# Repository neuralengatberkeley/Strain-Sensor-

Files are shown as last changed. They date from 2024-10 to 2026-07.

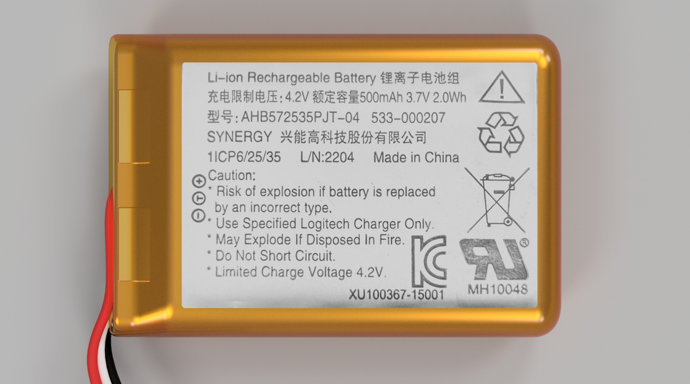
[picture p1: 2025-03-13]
CAD Files/tom sensor assembly/Renders/Battery 3.png

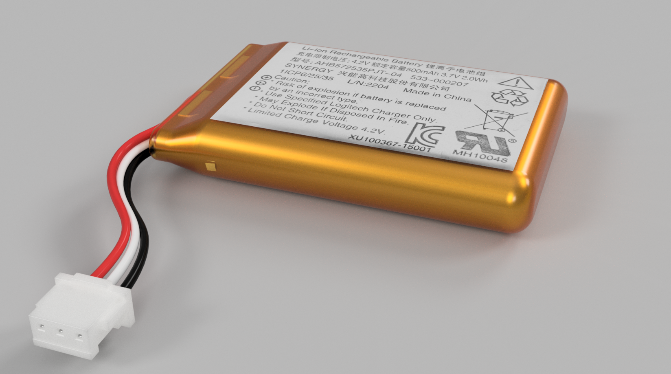
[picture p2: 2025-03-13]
CAD Files/tom sensor assembly/Renders/Battery 2.png

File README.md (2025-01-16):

# Strain-Sensor-

LMSG

# ABS Filmanent LM Channels:

3D printed ABS channels to be dissolved in acetone:  

abs filaments

CAD file for 3d prints shown in image above:  ...CAD Files/abs_lofted_insert/basic strain gauge 0p02.ipt

3D printer used -> Original Prusa MK4s

# Strain Sensor Fabrication Procedure:

LMSG fab process

wire insertion and sealing

#  Auto Bender:

All Structural parts (e.g. plates, shaft collars, fasteners) were purchased from goBILDA:  https://www.gobilda.com/

auto bender parts

# AutoBender Sensor Circuit:

autobender sensor circuit

# AutoBender PCB (which inlcudes sensor circuit and servo circuit):

AutoBender PCB design can be found here in ...Fritzing Files/Voltage Divider PCB/bender PCB.fzz

# Interpreting CSV Data File Columns:

Column A:  Disregard.  It was initially meant to provide the theoretical bend angle, but it is wrong and not used in any calculation.

Column B:  Adafruit BNO055 IMU Pitch Euler Angle (degrees)

Column C:  ADC Value as read from Adafruit Sensor MCP3421 18-Bit ADC (The ADC sensor is in parrallel with the Liquid Metal Strain Gauge (LMSG).  The LMSG is in series 			with a 100 ohm resistor).  Since the code is set to read 14-bits, the possible range of values is from 0 to 2^14 - 1.

Column D:  ADC Value as read from Hall Effect Rotary Encoder (https://p3america.com/erc-series/?srsltid=AfmBOoqSsWeZSXtsMrmoHyB0DRfSCzyFlUfcnEff0gpcv0NyMvrGhVz7).  The 		rotary encoder can rotate from 0 to 320 degrees.  There is a mechanical stop at 0 and 320 degrees.  Since the rotary encoder is connected directly to 			Arduino Uno, the adc output from the Arduino can have values from 0 to 2^10 - 1.  

Note about converting rotary encoder adc value to angle in degrees:  

rot encoder

As a result of this calculation, the rotatry encoder angle should always start at 0 degrees.  The initial IMU angle in degrees typically starts around ~ 3 degrees.  

# Derivation of Change in Resistance Formula as a Function of Axial Strain:

formula part 1

If an axial load is applied to a solid in the x-direction, the solid's lateral dimensions in the y- and z-directions will typically contract, depending on the material properties. The ratio of lateral contraction (negative strain) to axial extension (positive strain) is called Poisson's ratio. The definition includes a negative sign, ensuring that Poisson's ratio is a positive value for materials that contract laterally when stretched axially. 

Poisson's Ratio

formula part 2

References:  

1. Soft Robotics Toolkit. (n.d.). Casting soft robots. Retrieved January 14, 2025, 
	from https://softroboticstoolkit.com/book/export/html/206021
2. Craig Jr., R. R. (2011). Mechanics of materials (3rd ed.). Wiley.
3. Hambley, A.R. (2011). Electrical Engineering Principles and Applications (5th ed.).  Prentice Hall.
4. Callister Jr., W. D., & Rethwisch, D. G.  Materials Science and Engineering: An Introduction (10th ed.).  Wiley.
5. Chen, J., Zhang, J., Luo, Z., Zhang, J., Li, L., Su, Y., Gao, X., Li, Y., Tang, W., Cao, C., Liu, Q., Wang, L., & Li, H. (2020). 
	Superelastic, sensitive, and low hysteresis flexible strain sensor based on wave-patterned liquid metal for 
	human activity monitoring. ACS Applied Materials & Interfaces, 12(19), 22200–22211. 
	https://doi.org/10.1021/acsami.0c04709

# Explanation of Model Developed for Axial Strain as a Function of Bend Angle:

The finger joints are modeled as a hinged joint where the leaf rotation axis is concentric with the knuckle axis.  Additionally, the interial surface of the leaf is in contact with the exterior surface of the knuckle.  The change in length of the sample is calculated from the arc length forumla. This model is presented in the image below:

Human Knuckle Model

However, in our autobender, the interior rotating surface of the leaf is offset from the exterior surface of the knuckle by an amount delta.  The adjusted AutoBender model is presented in the image below:  

Auto Bender Model

# Expected Trend for Normalized Resistance vs Axial Strain:

The plot below shows theoretical curves of normalized resistance versus axial strain for samples with varying lengths L, but identical liquid metal channel length (Lo) and cross-sectional area (A). The following trends are observed:

1.  As sample length, L, increases (assuming same liquid metal channel lengths and cross-sectional area), the slope of the curve decreases.
2.  A longer sample will experience less axial strain at a 90 degree bend angle
3.  For axial strains below approximately 40% (e.g., in human knuckle models), the relationship can be approximated as linear.
4.  As bend radius (R in this case, not r as indicated in human knuckle model image :/) increases, axial strain also increases for the same bend angle. For example, a strain sensor on a larger knuckle would experience greater axial strain compared to one on a smaller knuckle.  

res vs strain trends

# "Gluing" LMSG on to fingers:

"paint" Derma-Tac (https://www.smooth-on.com/products/derma-tac/) AND Skin-Tite (https://www.smooth-on.com/products/skin-tite/) onto finger, place sensor on finger for a couple minutes until cross-linking occurs

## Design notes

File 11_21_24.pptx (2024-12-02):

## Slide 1

Human Knuckle Model

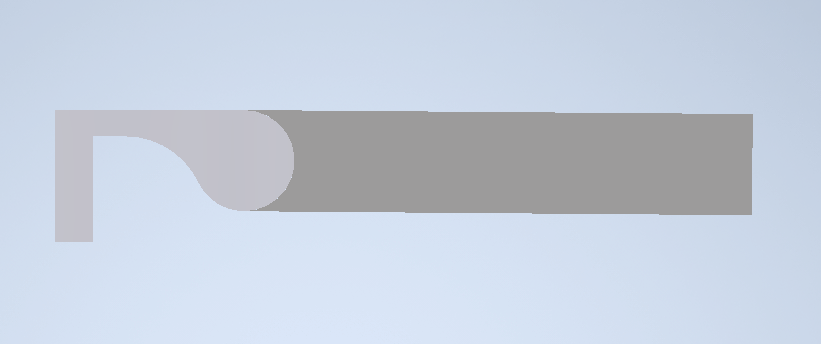
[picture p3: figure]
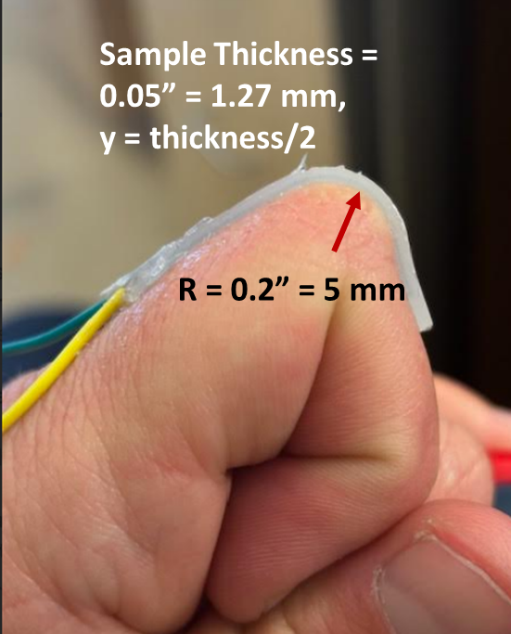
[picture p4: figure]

L_o =1.67"

h = 0.05” (1.27 mm)

R = 0.125”

θ

Measured Strain on finger with sample abs_100
(using strings)
~ 0.1677 or 16.8%

ε_x =((R+h)θ)/(L_o)=(ΔL)/(L_o)

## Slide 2

Auto Bender Model

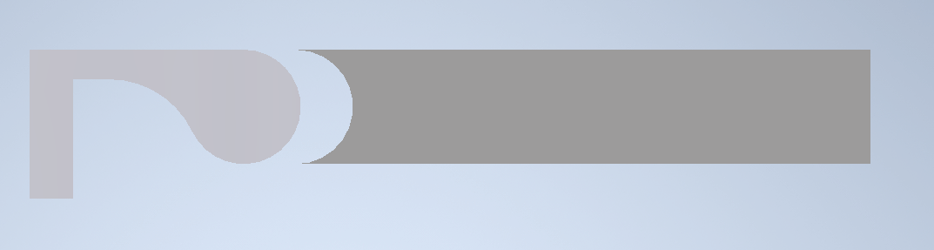
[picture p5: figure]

h

R

δ = 0.25”

θ

Measured Strain on sample abs_100 on AutoBender
~ 0.4 or 40%

ε_x =((R+h+δ)θ)/(L_o)

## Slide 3

As a reminder….Sample ABS_100

40% elongation

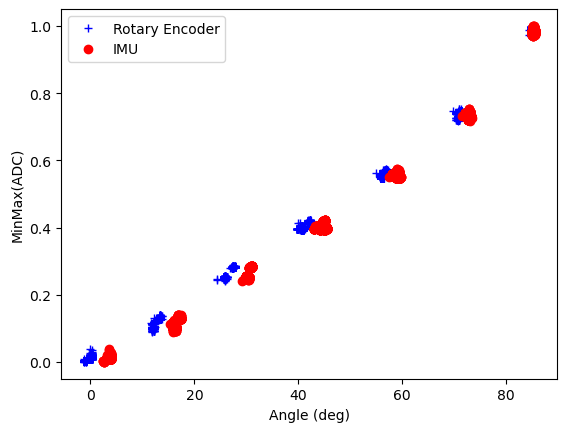
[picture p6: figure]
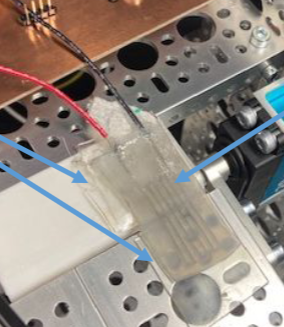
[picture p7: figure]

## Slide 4

L_o =length of LM channel

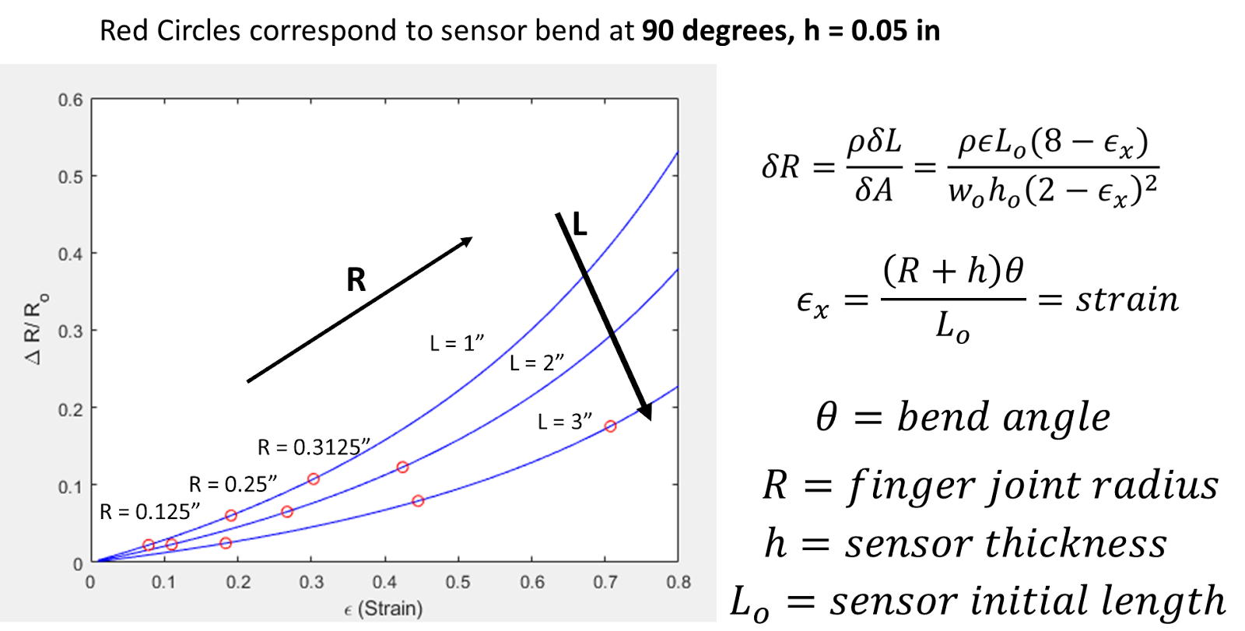
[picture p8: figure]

Previous slide results strained to 40% elongation at L = 1.67”

Sample Length (not LM channel length)

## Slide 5

Wire Lead Gauge size CHANGED TO = 30 (from 28)

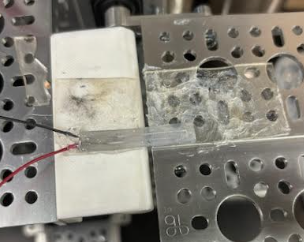
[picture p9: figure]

New Sample 11_21_2024

44.5% elongation

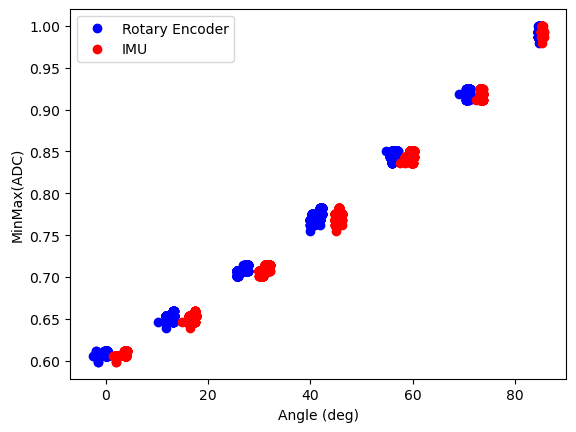
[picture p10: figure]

0.25” width

1.5” sample length

0.02” x 0.02” square cross-section channels

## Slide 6

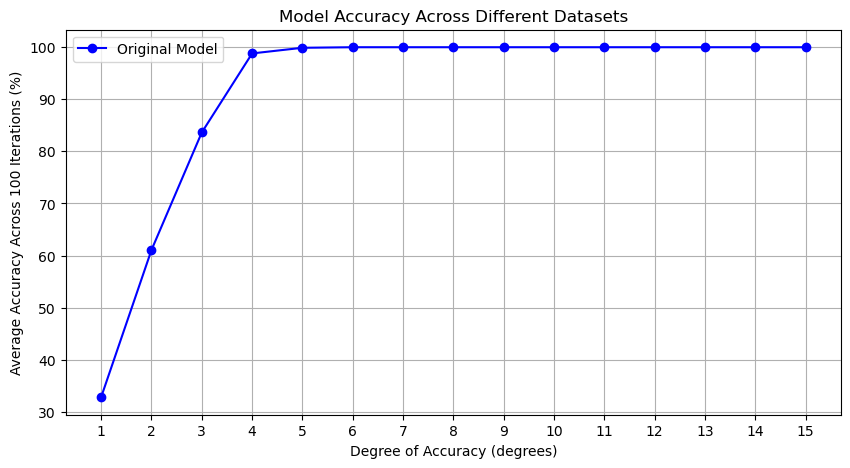
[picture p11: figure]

## Sample 2.27” Long -> will test Monday

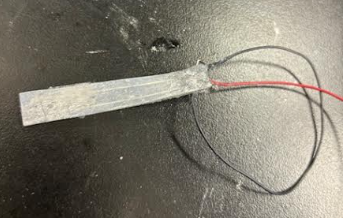
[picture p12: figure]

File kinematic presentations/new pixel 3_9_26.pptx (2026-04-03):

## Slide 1

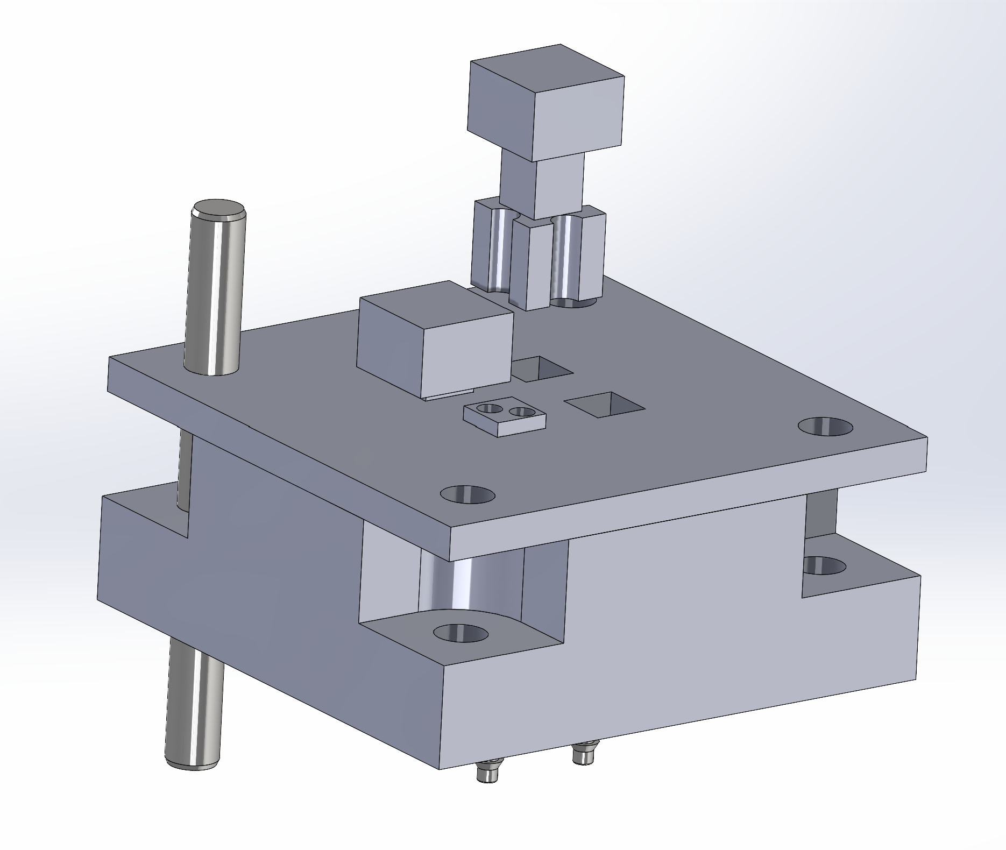
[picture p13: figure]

Head of pixel (not shown) should have two long set screws that attach to head of pixel

If pixel made of hardened stainless steel, 0.01 lb weight.

Press-fit steel dowel
pin for precision
location matching

Channels for air to flow through and provide lateral stabilization like an air hockey table would for the puck

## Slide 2

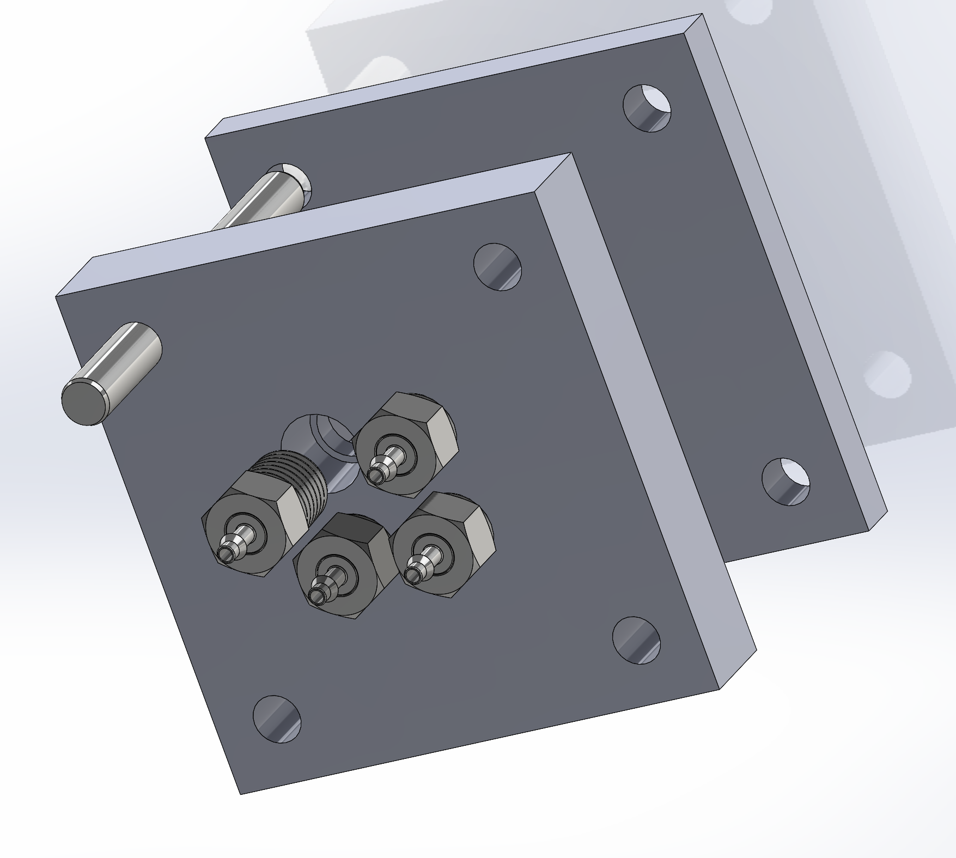
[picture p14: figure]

Pipe thread…never coming out. Compressed air pushes on pixel directly to lift up

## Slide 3

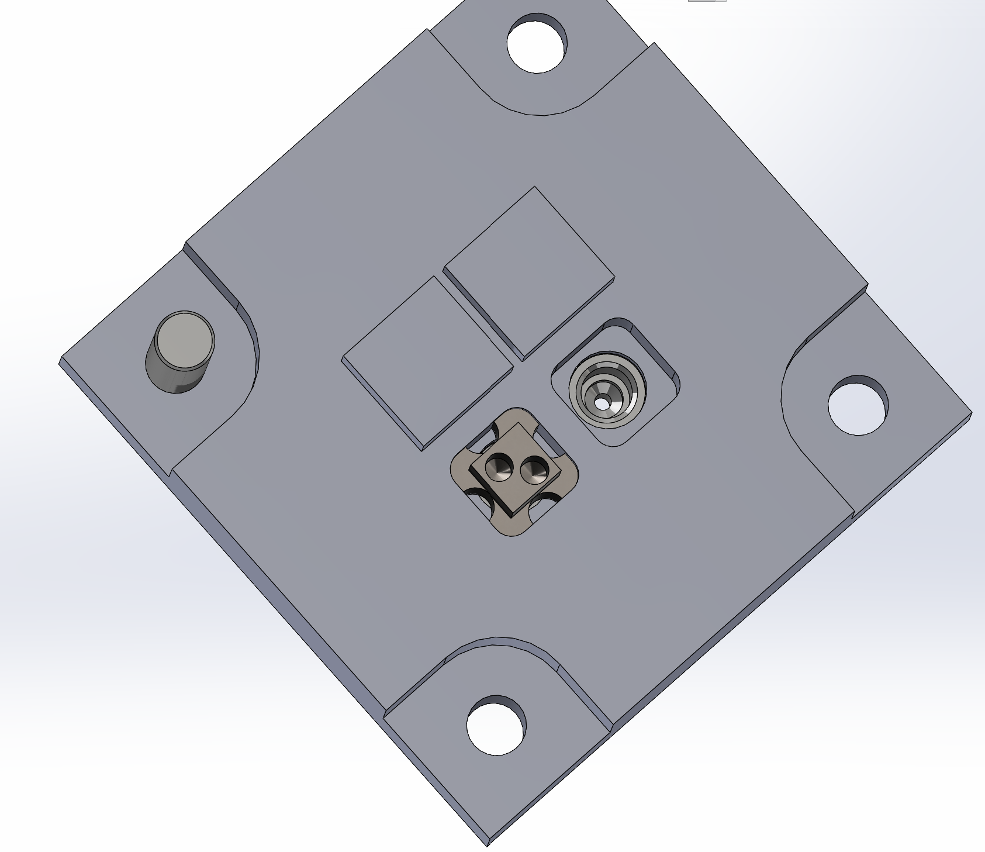
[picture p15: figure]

Compressed air from below pushes up and provides lateral resistance

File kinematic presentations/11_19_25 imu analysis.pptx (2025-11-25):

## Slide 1

Strain Gauge Results:
Likelihood Threshold DLC Positions: 0.4 (increase this and number of pts in time series decreases)
Calibration angles: 0-> 67.5

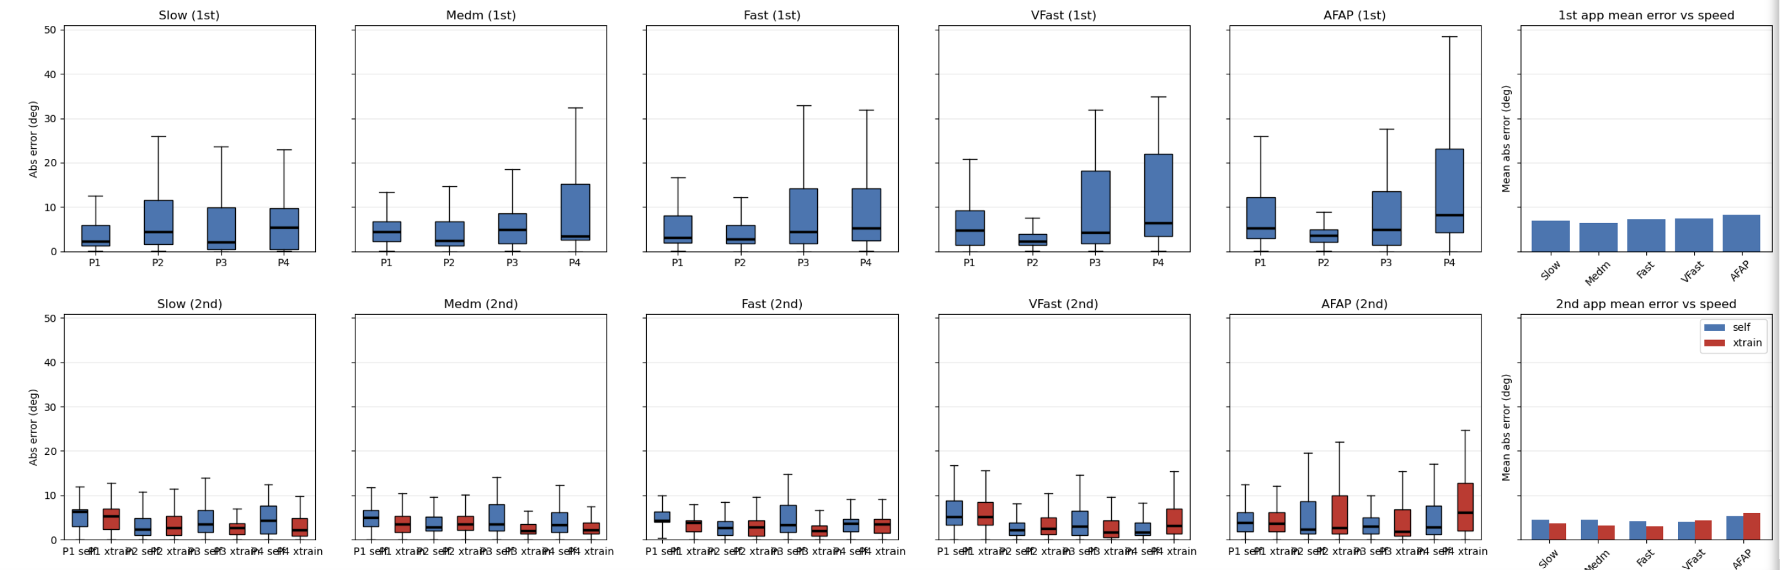
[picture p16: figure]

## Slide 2

1st Alignment: Timestamp Alignment

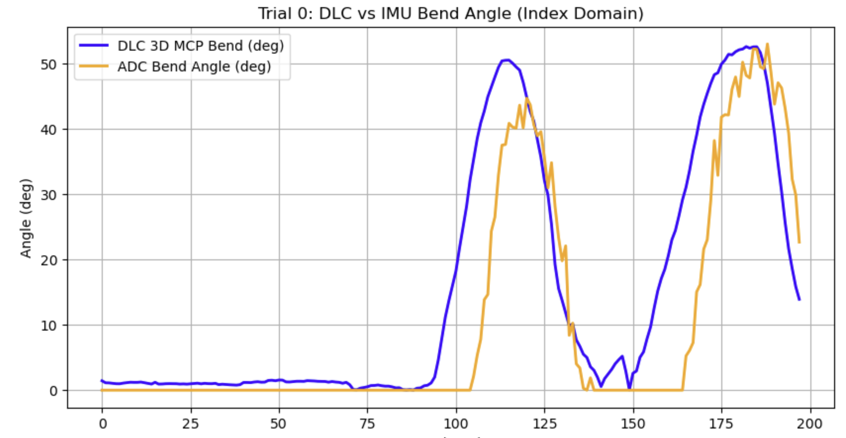
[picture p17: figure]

2nd Alignment: Shift entire series until error is minimized

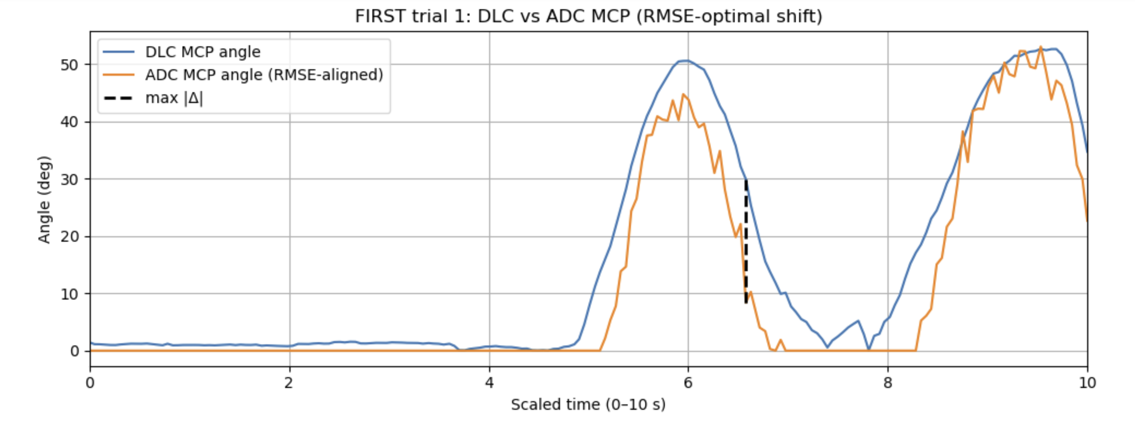
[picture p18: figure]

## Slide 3

Strain Gauge Calibrations

Blue = 1st calibration

Orange = 2nd calibration

P3

P4

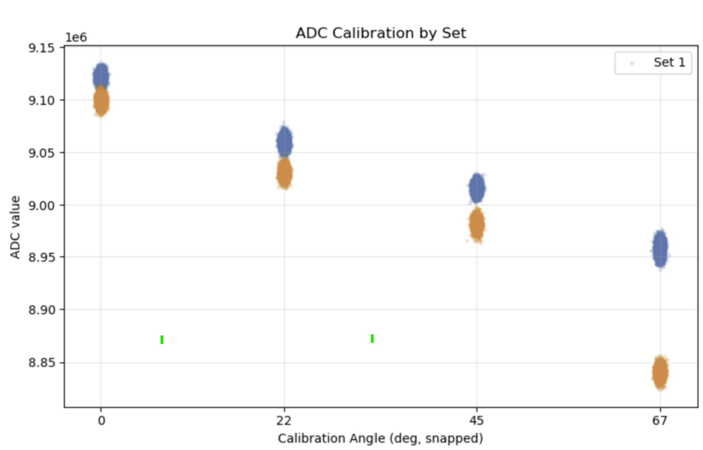
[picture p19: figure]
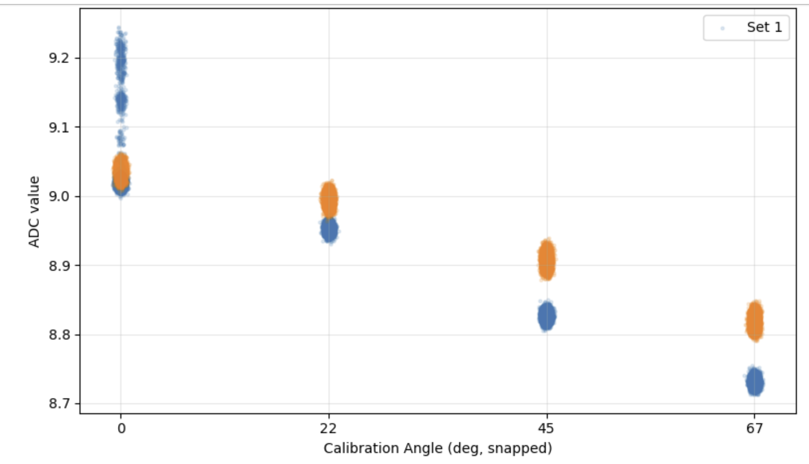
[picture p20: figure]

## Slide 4

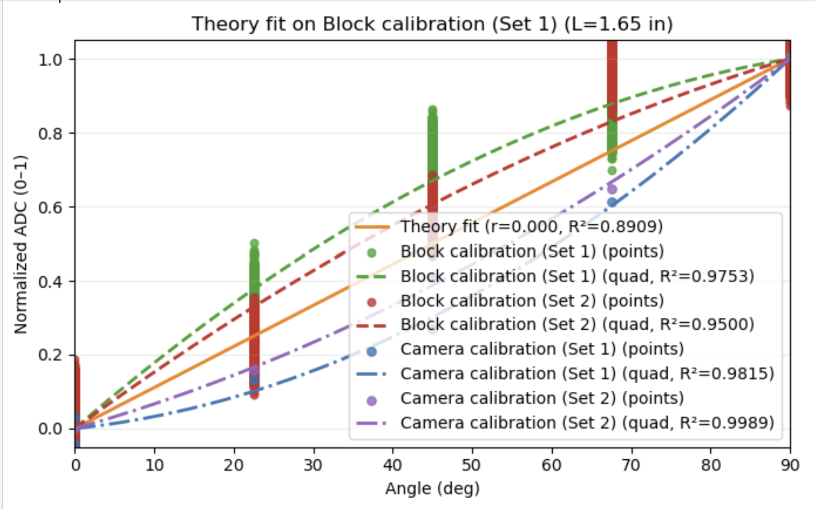
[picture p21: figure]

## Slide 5

Occasionally saw this….disconnection?

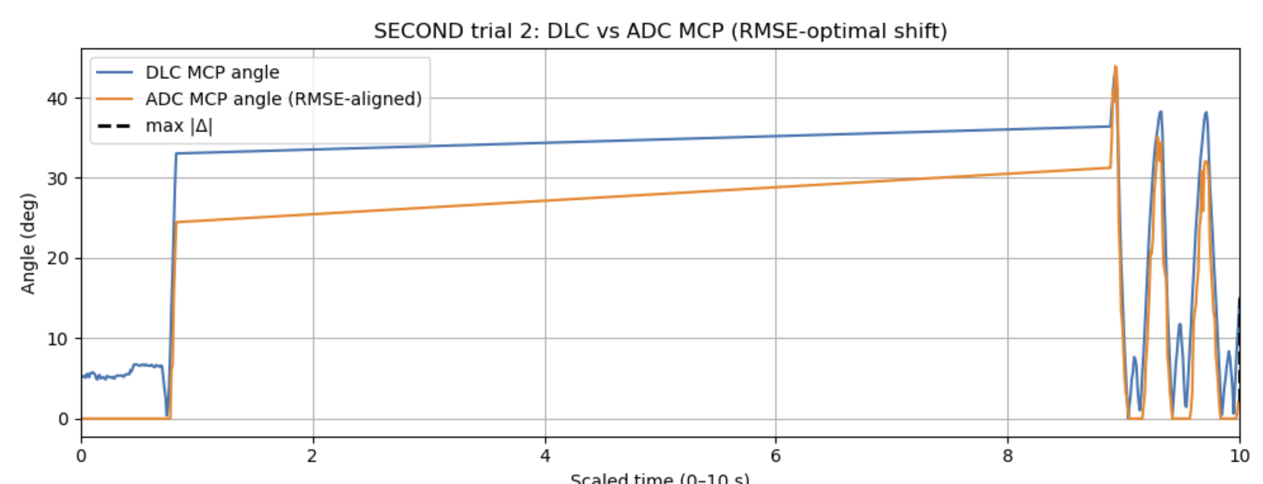
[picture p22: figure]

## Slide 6

IMU Results:
Likelihood Threshold DLC Positions: 0.4
Angle calc:
1. Quaternions to rotation matrices.
2. change of basis for palm imu frame to wrist imu frame.
3. Calculate relative angle between vectors vwrist = [0 1 0] vs vpalm = [0 1 0] represented in wrist frame
4. Steel need to project palm vector to single plane (to get out flexion vs abduction)
5. Subtract baseline (starting IMU angle from time series so all angles start at 0 deg)

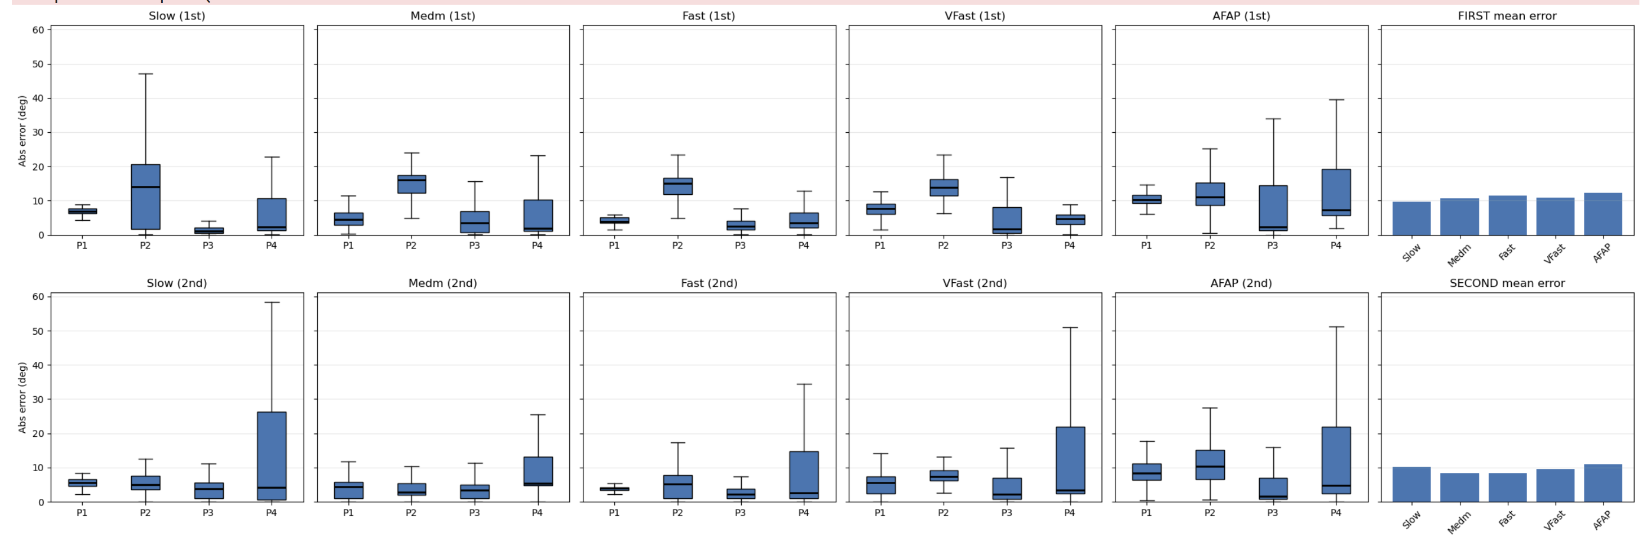
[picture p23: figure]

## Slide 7

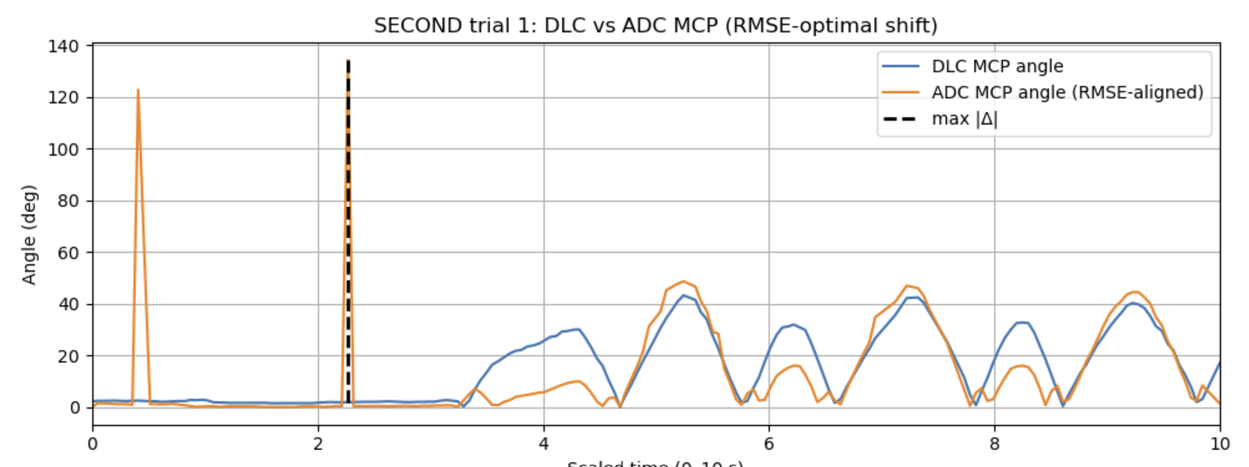
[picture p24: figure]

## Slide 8

- Frames:
  - F : fixed IMU frame (wrist)
  - M : moving IMU frame (palm)
  - W : world frame
- Rotation matrices:
  - R_F : maps vectors from wrist frame → world v_W =R_F v_F
  - R_M : maps vectors from palm frame → world v_W =R_M v_M
- Axes you chose:
  - e_F : a unit vector along the chosen axis in the wrist frame e.g. e_F =[0, 1, 0]^T , for the y-axis
  - e_M : a unit vector along the chosen axis in the palm frame e.g. e_M =[0, 1,0]^T ,

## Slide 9

From the quaternions you get, at each time t :
- R_F (t) : rotation of the wrist IMU
- R_M (t) : rotation of the palm IMU
By convention:
v_W =R_F (t) v_F , v_W =R_M (t) v_M .
So R_F and R_M tell you how each IMU’s body axes sit in the world.

Start from palm → world:
v_W =R_M v_M .
Then world → wrist:
v_F =R_F^(⊤) v_W .
Combine:
v_F =R_F^(⊤) R_M v_M .
So the relative rotation matrix is:
R_(rel) =R_F^(⊤) R_M ,
and it satisfies:
v_F =R_(rel) v_M
for any vector v_M defined in the palm frame.

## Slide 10

You chose a moving-axis e_M in the palm frame (e.g. its y-axis).
To see that axis from the wrist’s perspective, use the relative rotation:
v(t)=R_(rel) (t) e_M
Here:
- e_M is the axis in the palm frame,
- v(t) is that same physical axis, now expressed in the wrist frame.

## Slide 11

For intuition: compute the angle in the world frame:
- Wrist axis in world:
a_W (t)=R_F (t) e_F
- Palm axis in world:
b_W (t)=R_M (t) e_M
Then:
cosθ(t)→ a_W (t)⋅b_W (t).

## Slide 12

q_1 =[w_1 x_1 y_1 z_1 ]=wrist quaternion

q_2 =[w_2 x_2 y_2 z_2 ]=palm quaternion

q_(rel) =q_1^(−1) ⨂q_2 , where q_1^(−1) =[w_1 −x_1 −y_1 −z_1 ]

θ_(rel pitch) =sin^(−1) [2[w_(rel) y_(rel) −z_(rel) x_(rel) ]]

roll (X) = atan2( 2(w x + y z), 1 - 2(x² + y²) )
pitch (Y) = asin( 2(w y - z x) )
yaw (Z) = atan2( 2(w z + x y), 1 - 2(y² + z²) )

Kuipers, J. B. (1999). Quaternions and Rotation Sequences. Princeton University Press.
Chapter 5: Rotations, Relative Rotations, and Quaternion Algebra

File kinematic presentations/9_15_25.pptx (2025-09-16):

## 9/15/2025

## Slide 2

1st Autobender Strain Calibration

1st Hand on Autodender Strain Calibration

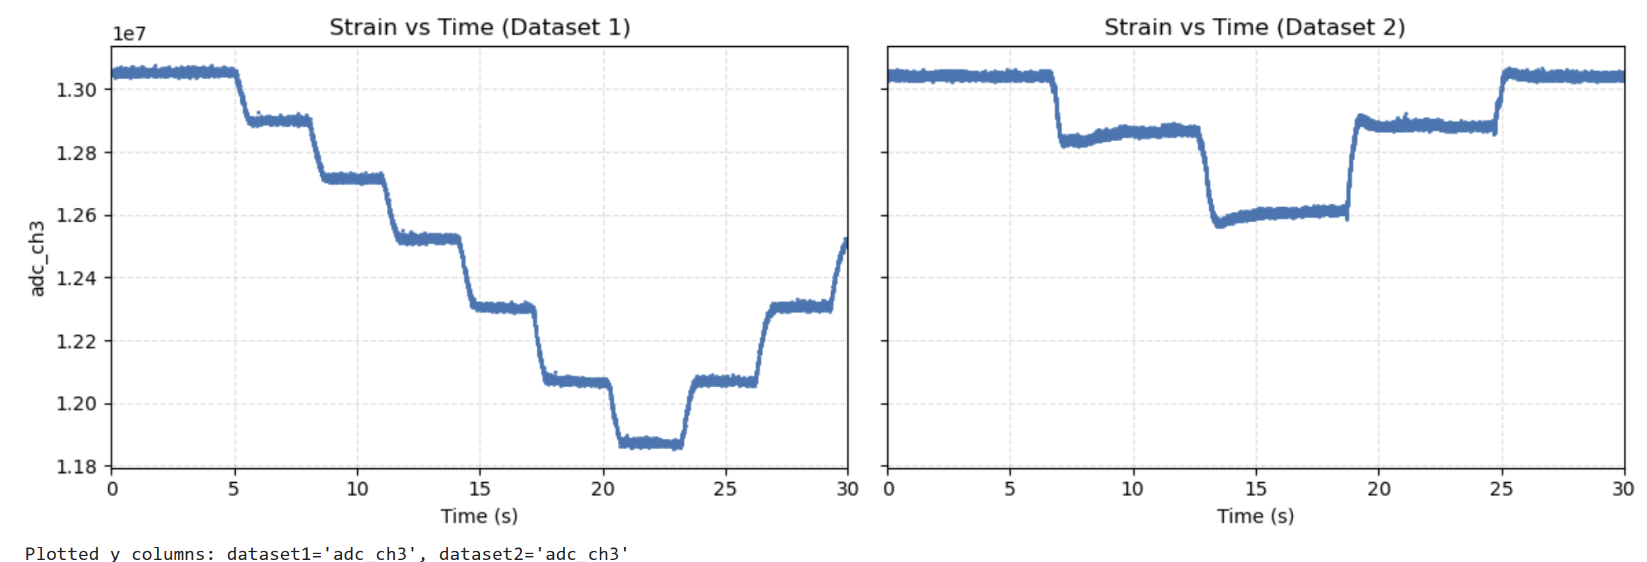
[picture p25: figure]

## IMU’s on Autobender

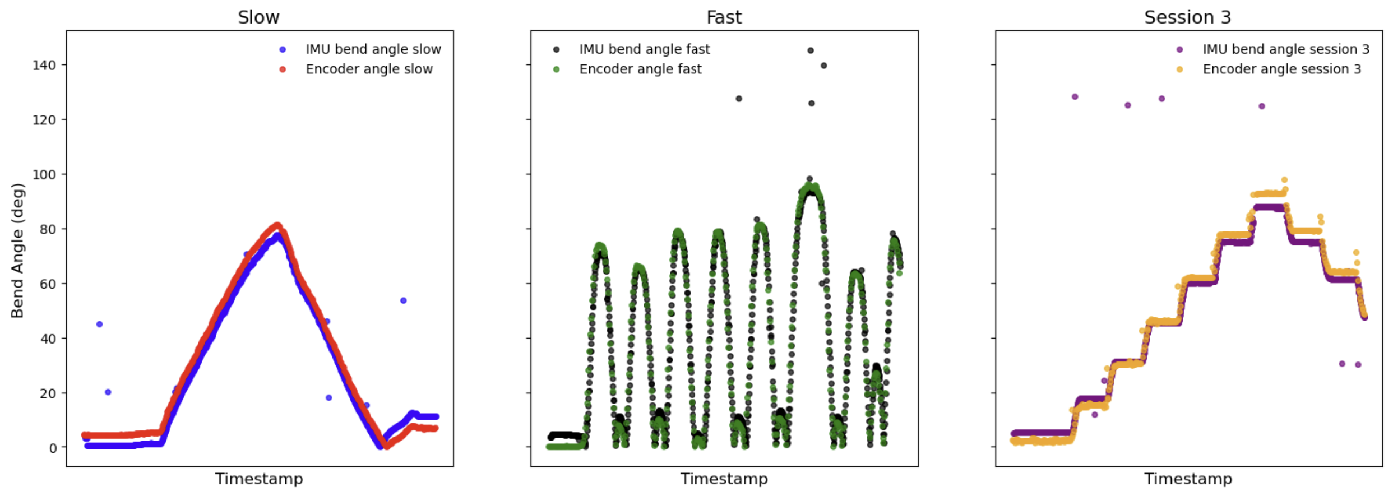
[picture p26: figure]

## IMU’s on Autobender


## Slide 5

1st Autobender Strain Calibration Curve Fit of Raw Data

1st Hand on Autodender Strain Calibration
Curve Fit of Raw Data


If not including data between autobender jumps (data recorded continuously, unlike autobender studies last year where data only recorded every 15 degs), curve fit improves drastically.

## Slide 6

Autobender Norm 0 to 1 model used to fit Hand Norm 0 to 1 Data, as in previous data


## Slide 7

ε=αθ, where α=c/L , epsilon=strain or(ΔL)/L, c=knuckle radius, L=sample length

(ΔR)/(R_o)=(ρLε)/(whR_o)[(8−ε)/((2−ε)^2)]=k, where R_o =initial resistance

norm_(o→1) =(k_i −k_(min))/(k_(max) −k_(min))=(θ_i (8−αθ_i )(2−(απ)/2)^2)/(π/2(8−(απ)/2)(2−αθ_i )^2)

norm_(@1) =(k_i (θ_i =π/2)−0)/(k_(max) (θ_i =π/2)−0)=1

norm_(@0) =(k_i (θ_i =0)−0)/(k_(max) (θ_i =π/2)−0)=0

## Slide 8

Theoretical Model used To Fit Autobender (Left) and Hand (Right) Data

1st Autobender Theor Curve Fit of Raw Data


1st Hand on Autodender Theor
Curve Fit of Raw Data


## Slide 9


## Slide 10

Predicted Angle Based on Measured Knuckle Radius

norm_(o→1) =(θ_i (8−αθ_i )(2−(απ)/2)^2)/(π/2(8−(απ)/2)(2−αθ_i )^2)

Measured Radius

From raw adc

Abs Error


## 1 Trial of Bending Finger AFAP


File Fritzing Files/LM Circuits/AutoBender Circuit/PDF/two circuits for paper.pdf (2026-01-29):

A

100ohms; Strain Sensor; LMC648; PGA=2; Adafruit MCP3421; 2.048V Ref; Arduino Uno I2C; x75 Gain; Arduino Uno 5V

B

Strain Sensor; OPA333; PGA=2; 2ohms; 2.048 Vref; RPi SPI; x69 Gain

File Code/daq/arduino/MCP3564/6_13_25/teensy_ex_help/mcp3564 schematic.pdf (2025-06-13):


Arduino Uno (not Teensy)

10K pullup on SDO (3.3 ->
10k -> MISO-> Arduino Uno
reads SDO

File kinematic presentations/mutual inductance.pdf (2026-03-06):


thin kapton tape with metal plated traces or threaded wires to tape to controller? Stiffness small, top LC receives AC current, creates Mag field

thin rubber sticker with coil/cap embedded. This part stuck to skin. As knuckle bends, it pulls bottom coil away from top coil, changing resonant frequency magnitude. Bottom LC is being mutually inducted

"2-aixs Wireless" E-skin Bend Sensors -
Taking Advantage of Resonant Frequency Shifts from Mutual Inductance + Difference in Spring Stiffness's

k1
k2

Springs in Series
k2 >> k1 so that effect
of pip bend much
greater than mcp, so
can "directly" measure
pip

k1

k2

2x (as small as 3mm in
dia) Inductor in parallel
with capacitor LC
resonator

as LC pads separate
due to finger bending,
resonant frequency
shifts because center
to center distance
changes

IMU

AC Current @
resonant frequency

Mutual inductance suppressed stacked inductors for passive wireless multi-
parameter sensors | IEEE Conference Publication | IEEE Xplore


Top LC slides

Top LC Rotates

1. Overall Sensor Idea: Use mutual inductance to measure resonant frequency shifts
a. One 2d circular coil emits a mag field and tag coil underneath gets resonated and emits resonant frequency back to top coil.
b. If centers of coils shift, resonant frequency changes
2. arrange emitter/reader coils in 2x2 arrangement and place above 1 tag coil
a. This will read 4 frequencies and can then detect 2d position, calibrate to flexion and abduction
3. Make use of two different stiffness material where smaller stiffness to place metal sputter coated traces to glue on arm. replace actual wires.


2D Position Sensor -> calibrate to flexion/ abduction. So 2x2 emitter/readers over 1 tag coil. 2x2 gives distribution of field over each.


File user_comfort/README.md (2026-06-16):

# user_comfort

Plots and stats for application/ removal times and survey ratings.

Python 3.13.2

## Layout
- `data/` — CSV inputs (`app_times.csv`, `rem_times.csv`, `ratings.csv`)
- `notebooks/` — analysis notebook(s) -- 01 for initial plots, 02 for figure formating  
- `src/kin_tools/` — reusable code (utils, plotting, stats)
- `out/` — saved figures and tables

#### LME stats: https://www.statsmodels.org/stable/mixed_linear.html

#### Data collected here in 'Sheet1': https://docs.google.com/spreadsheets/d/1FZ8wFQWQy3xjgIYyGS5vvDAiU_qLpCyN-fVS316duq8/edit?usp=sharing

## Project tree: 
kinematics/user_comfort/
├─ data/
│  ├─ app_times.csv
│  ├─ rem_times.csv
│  └─ ratings.csv
├─ notebooks/
│  └─ 01_all_plots_and_stats.ipynb       # all plots shown here
├─ out/                                  # figures get saved here
├─ src/kin_tools/
│  ├─ __init__.py
│  ├─ utils.py
│  ├─ palettes.py
│  ├─ io.py
│  ├─ plotting.py                       # 
│  └─ stats.py                          #
└─ requirements.txt

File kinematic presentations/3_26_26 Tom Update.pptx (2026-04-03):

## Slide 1

11-7


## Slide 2

11-4


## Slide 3

11-2


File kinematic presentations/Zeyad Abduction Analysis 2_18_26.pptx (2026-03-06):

## Zeyad Abduction Analysis

2_18_26

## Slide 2


First Application Data

Second Application Data

First Application Data, first trial (3 trials in total: 0, 1, 2)-> (Pandas DataFrame)

theta_cam_cal: ADC Data converted to angles with calibration curve

## theta_cam_cal: ADC Data converted to angles with calibration curve

- theta_cam_cal is a column within the adc_first_theta[0] Pandas Dataframe
  - You could create a new pandas dataframe and copy that column into it:
    - df_new = adc_first_theta[0][["theta_cam_cal"]].copy()
  - Give that column a new name:
    - df_new.columns = [“11_2_app1_trial_1"]


## Append Trial Columns


## Example of Taking Standard Deviations per column


## Take Mean and Std of column Std’s


## So Overall Plan

- Each Participant will have 2 applications and 3 trials per application
  - Within each trial there should be two distinct regions:
    - (1) Rest region
    - (2) Abduction moving region -> cycle 0 to 20 deg
- We want to compare overall region of non-moving to moving
  - We can accomplish that by doing the following:
    - Take std of non-moving regions AND moving regions for each participant/application/trial
    - put all those std’s into a new dataframe
    - We will do a stat/hypothesis testing significance analysis where we compare non-moving region for all participants to moving region
    - Question is: Does abduction significantly affect changes in angle measurement?

## Videos

- We need to be able to clearly identify regions/timestamps/frames in videos where movement begins
- Each trial lasted exactly 10 sec because that is how we programmed the daq code in Rpi
- Video Frame Extractor Code: Google how to do this

## Zeyad Abduction Analysis

3_5_26

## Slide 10

1. Conver x-scale to 0-10 sec for each application, trial, participant. Take 10 sec and divide by total number of data in trial, and that will give a time for each data point.

2. Try re-plotting all applications / trials with vertical line separating non-moving from moving section. Should look something like below.


3. Split each set of data to non-moving and moving data and take std of each. Put those std values into new data frame where column 0 might be participant, column 1is application 0 or 1, column 2 is trial # (0,1,or 2). Column 3 is std of non-moving. Column 4 is std of moving.

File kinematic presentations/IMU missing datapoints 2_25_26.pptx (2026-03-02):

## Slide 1


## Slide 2


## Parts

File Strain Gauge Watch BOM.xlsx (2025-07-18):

Strain Gauge Circuit
1x | ADC | AD7124-8 (we will use 4 diff pairs for now) | AD7124-8 Eight-Channel, Low Noise, Low Power, 24-Bit ∑-Δ ADC with On-Chip In-Amp and Reference | Analog Devices (https://www.analog.com/en/products/ad7124-8.html)
4x | OpAmp | OPA333 (will double check gain value next week) | OPA333 data sheet, product information and support | TI.com (https://www.ti.com/product/OPA333)
4x | Current Source | LT3092 (set for 7.5mA) | LT3092 Datasheet and Product Info | Analog Devices (https://www.analog.com/en/products/lt3092.html)
1x | Precision Voltage Ref (for each 4 channels In-) | MAX6070 (2.048V) (need to use ceramic caps of specific type) | MAX6070 Datasheet and Product Info | Analog Devices (https://www.analog.com/en/products/max6070.html)

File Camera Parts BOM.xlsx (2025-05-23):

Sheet: modified
Teledyne Flir Blackfly S USB3 1.6MP Color Camera (used) |  | B&H | 2 | 256.95 | 513.9 | https://www.bhphotovideo.com/c/used/1844599/teledyne_flir_bfs_u3_16s2c_cs_blackfly_s_usb3_1_6mp.html
LENS: Tamron 8 mm, 1/1.8", 5 MP, C-mount Lens | LENS-80T4C / Tamron M118FM08 | B&H | 2 | 163.95 | 327.9 | Tamron M118FM08 Mega-Pixel Fixed-Focal Industrial Lens M118FM08 (https://www.bhphotovideo.com/c/product/725574-REG/Tamron_M118FM08_M118FM08_Mega_Pixel_Fixed_Focal_Industrial.html)
CS to C Mount Adaptor for Lens (https://www.teledynevisionsolutions.com/products/cs-to-c-mount-5mm-spacer-adapter/?model=ACC-01-5004&vertical=machine%20vision&segment=iis) |  | Teledyne | 2 | 11.8 | 23.6 | Optic Mount: CS- to C-mount Adapter | Teledyne Vision Solutions (https://www.teledynevisionsolutions.com/products/cs-to-c-mount-5mm-spacer-adapter/?model=ACC-01-5004&vertical=machine%20vision&segment=iis)
GPIO Cable 1 meter: GPIO Cables with 6-pin Hirose HR10 Connector | ACC-01-3009 | Teledyne | 2 | 48.8 | 97.6 | GPIO Cables with 6-pin Hirose HR10 Connector | Teledyne Vision Solutions (https://www.teledynevisionsolutions.com/en-ca/products/hirose-hr10-6-pin-circular-connector/)
USB 3.1 Locking Cables 3 meters | ACC-01-2300 | Teledyne | 2 | 24.6 | 49.2 | USB 3.1 Locking Cables | Teledyne Vision Solutions (https://www.teledynevisionsolutions.com/products/usb-3.1-locking-cable/)
Tripod Adaptor: Blackfly S (39 mm) | ACC-01-0016 | Teledyne | 2 | 37.5 | 75 | Tripod Adapter: Blackfly S (39 mm) | Teledyne Vision Solutions (https://www.teledynevisionsolutions.com/products/tripod-adaptor-for-39mm-blackfly-s-models/?model=ACC-01-0016&vertical=machine%20vision&segment=iis)
Camera Tripod | ? | AMAZON / NEEWER | 2 | 16.09 | 32.18 | Amazon.com : NEEWER Super Clamp with 3" Dual Ballhead Magic Arm, Cold Shoe, 1/4" Threads, Phone/Action Camera Mount Adapter for Desk Tripod Tube Crossbar Gimbal Rods Compatible with SmallRig GoPro DJI, ST83 : Electronics (https://www.amazon.com/Ballhead-Threads-Crossbar-Compatible-SmallRig/dp/B0CB5JKTBH)
 |  |  |  | Cheapest Total | 1119.38
Brayden Lens BOM
Item: | Description: | #: | Cost: | Sub-Total: | Link:
Marshall Electronics 4MP 2.8-12mm Lens | Adjustable 4MP lens with a focal depth of 2.8-12mm | 1 | $139.99 | $139.99 | Marshall Electronics 4MP 2.8-12mm f/1.4 Varifocal VS-M2812-4MP (https://www.bhphotovideo.com/c/product/1698499-REG/marshall_electronics_vs_m2812_4mp_2_8_12mm_4mp_varifocal_cs.html)
Marshall Electronics 4MP 6-60mm Lens | Adjustable 4MP lens with a focal depth of 6-60mm | 1 | $169.99 | $169.99 | Marshall Electronics 6-60mm 3MP f/1.4 Varifocal Manual VS-M660 (https://www.bhphotovideo.com/c/product/1698501-REG/marshall_electronics_vs_m660_6_60mm_3mp_varifocal_cs.html)
 |  |  | Total: | $309.98

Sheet: original
Item | P/N | Company | Quantity | Cost (before S&H) | Total | Website
CAMERAS: Blackfly S USB3: 5 MP, Color, C-mount | BFS-U3-50S4C-C | Teledyne | 2 | 740 | 1480 | Blackfly S USB3: 5 MP, Color, C-mount | Teledyne Vision Solutions (https://www.teledynevisionsolutions.com/products/blackfly-s-usb3/?model=BFS-U3-50S4C-C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)
CAMERAS: Blackfly S USB3: 5 MP, Color, C-mount | BFS-U3-50S4C-C | B&H | 2 | 878 | 1756 | Teledyne Flir Blackfly S USB3 5MP Color Camera BFS-U3-50S5C-C (https://www.bhphotovideo.com/c/product/1845635-REG/teledyne_flir_bfs_u3_50s5c_c_blackfly_s_usb3_5mp.html)
LENS: Tamron 8 mm, 1/1.8", 5 MP, C-mount Lens | LENS-80T4C / Tamron M118FM08 | Teledyne | 2 | 342 | 684 | Tamron 8 mm, 1/1.8", 5 MP, C-mount Lens | Teledyne Vision Solutions (https://www.teledynevisionsolutions.com/en-ca/products/c_mount-11.8-inch-lenses/?model=LENS-80T4C&vertical=machine%20vision&segment=iis)
LENS: Tamron 8 mm, 1/1.8", 5 MP, C-mount Lens | LENS-80T4C / Tamron M118FM08 | B&H | 2 | 163.95 | 327.9 | Tamron M118FM08 Mega-Pixel Fixed-Focal Industrial Lens M118FM08 (https://www.bhphotovideo.com/c/product/725574-REG/Tamron_M118FM08_M118FM08_Mega_Pixel_Fixed_Focal_Industrial.html)
CS to C Mount Adaptor for Lens (https://www.teledynevisionsolutions.com/products/cs-to-c-mount-5mm-spacer-adapter/?model=ACC-01-5004&vertical=machine%20vision&segment=iis) |  | Teledyne | 2 | 11.8 | 23.6 | Optic Mount: CS- to C-mount Adapter | Teledyne Vision Solutions (https://www.teledynevisionsolutions.com/products/cs-to-c-mount-5mm-spacer-adapter/?model=ACC-01-5004&vertical=machine%20vision&segment=iis)
GPIO Cable 1 meter: GPIO Cables with 6-pin Hirose HR10 Connector | ACC-01-3009 | Teledyne | 2 | 48.8 | 97.6 | GPIO Cables with 6-pin Hirose HR10 Connector | Teledyne Vision Solutions (https://www.teledynevisionsolutions.com/en-ca/products/hirose-hr10-6-pin-circular-connector/)
USB 3.1 Locking Cables 3 meters | ACC-01-2300 | Teledyne | 2 | 24.6 | 49.2 | USB 3.1 Locking Cables | Teledyne Vision Solutions (https://www.teledynevisionsolutions.com/products/usb-3.1-locking-cable/)
Tripod Adaptor: Blackfly S (39 mm) | ACC-01-0016 | Teledyne | 2 | 37.5 | 75 | Tripod Adapter: Blackfly S (39 mm) | Teledyne Vision Solutions (https://www.teledynevisionsolutions.com/products/tripod-adaptor-for-39mm-blackfly-s-models/?model=ACC-01-0016&vertical=machine%20vision&segment=iis)
Camera Tripod | ? | AMAZON / NEEWER | 2 | 16.09 | 32.18 | Amazon.com : NEEWER Super Clamp with 3" Dual Ballhead Magic Arm, Cold Shoe, 1/4" Threads, Phone/Action Camera Mount Adapter for Desk Tripod Tube Crossbar Gimbal Rods Compatible with SmallRig GoPro DJI, ST83 : Electronics (https://www.amazon.com/Ballhead-Threads-Crossbar-Compatible-SmallRig/dp/B0CB5JKTBH)
 |  |  |  | Cheapest Total | 2085.48
Brayden BOM
Item: | Description: | #: | Cost: | Sub-Total: | Link:
Teledyne Flir Blackfly S USB3 1.6MP Color Camera | Used Flir camera with 1.6MP (CS Mount) | 2 | $256.95 | $513.90 | https://www.bhphotovideo.com/c/used/1844599/teledyne_flir_bfs_u3_16s2c_cs_blackfly_s_usb3_1_6mp.html
Marshall Electronics 4MP 2.8-12mm Lens | Adjustable 4MP lens with a focal depth of 2.8-12mm | 1 | $139.99 | $139.99 | Marshall Electronics 4MP 2.8-12mm f/1.4 Varifocal VS-M2812-4MP (https://www.bhphotovideo.com/c/product/1698499-REG/marshall_electronics_vs_m2812_4mp_2_8_12mm_4mp_varifocal_cs.html)
Marshall Electronics 4MP 6-60mm Lens | Adjustable 4MP lens with a focal depth of 6-60mm | 1 | $169.99 | $169.99 | Marshall Electronics 6-60mm 3MP f/1.4 Varifocal Manual VS-M660 (https://www.bhphotovideo.com/c/product/1698501-REG/marshall_electronics_vs_m660_6_60mm_3mp_varifocal_cs.html)
 |  |  | Total: | $823.88

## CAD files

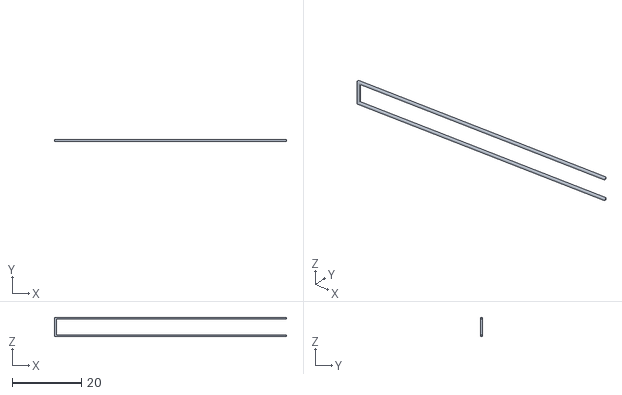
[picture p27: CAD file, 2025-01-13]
CAD Files/abs sample design for alignment/basic strain gauge 0p01 longest.stl
66.9 x 0.508 x 5.59

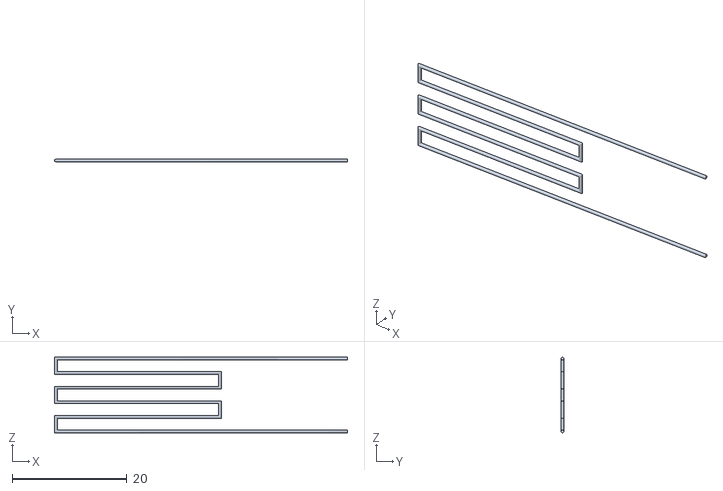
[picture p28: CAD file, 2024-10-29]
CAD Files/abs_100 Sample/strain guage abs.stl
51.1 x 0.508 x 13.2

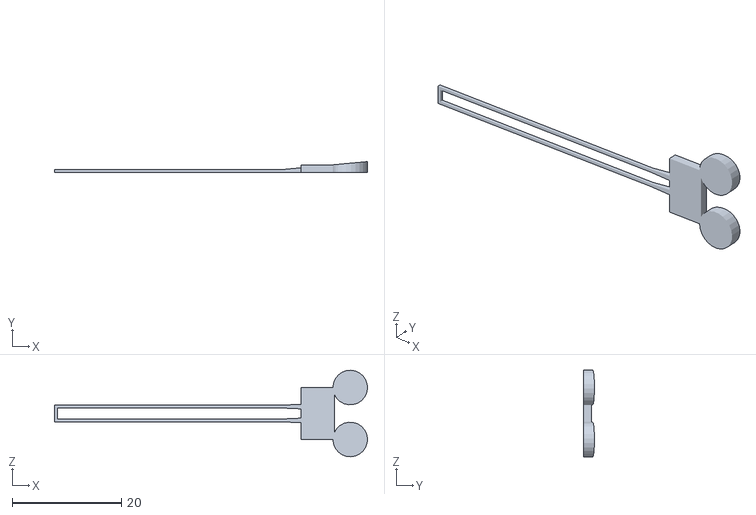
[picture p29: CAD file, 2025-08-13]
CAD Files/abs_lofted_insert/basic strain gauge 0p02 w align.stl
57.4 x 1.99 x 15.9

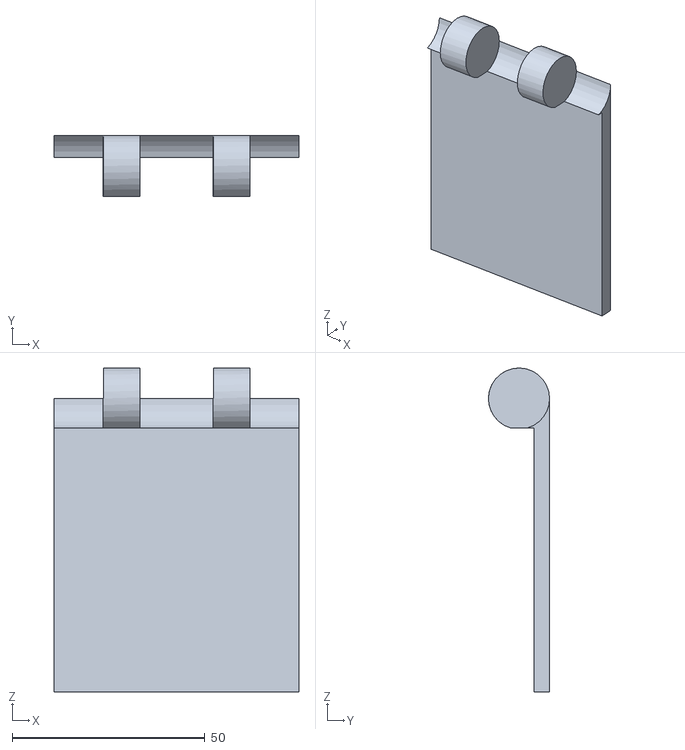
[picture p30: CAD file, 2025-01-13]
CAD Files/auto bender part files/knuckle plate hinge 2.stl
63.5 x 15.9 x 84.1

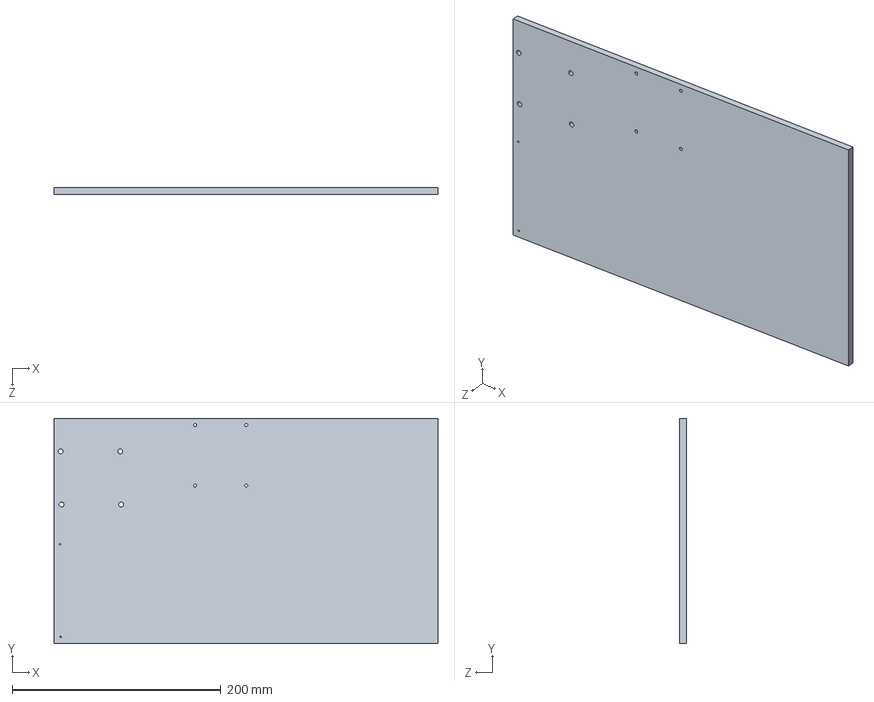
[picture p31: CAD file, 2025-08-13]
CAD Files/electronics plate/electronic plate.SLDPRT
368.3 x 215.9 x 6.35 mm

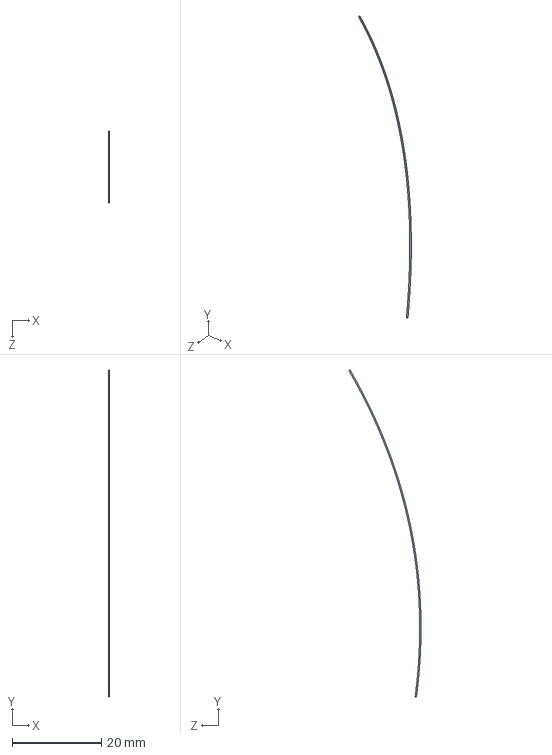
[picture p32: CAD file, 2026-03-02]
CAD Files/sensor fab/red wire.SLDPRT
0.317 x 73.4 x 16.2 mm

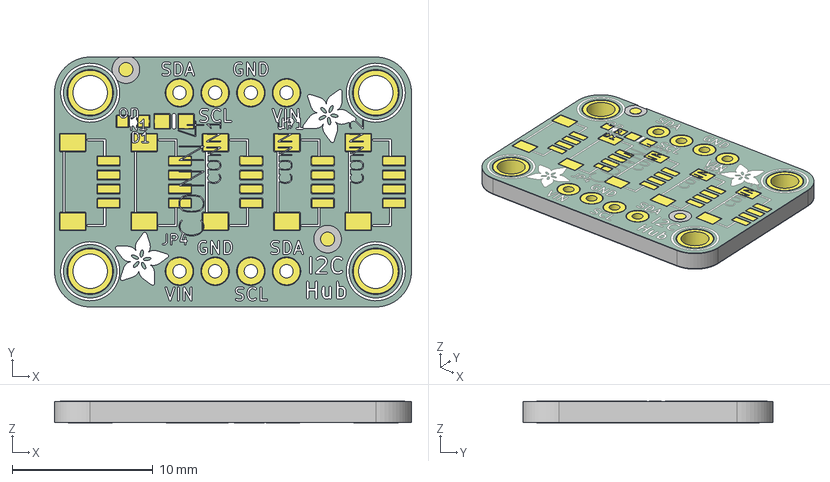
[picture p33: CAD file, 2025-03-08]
CAD Files/sensor fab/volt div breakout board/Adafruit Stemma QT 5 Port Hub.step
25.4 x 17.8 x 1.66 mm
Adafruit Stemma QT 5 Port Hub_copper
Adafruit Stemma QT 5 Port Hub_silkscreen
Adafruit Stemma QT 5 Port Hub_soldermask
Adafruit Stemma QT 5 Port Hub_PCB

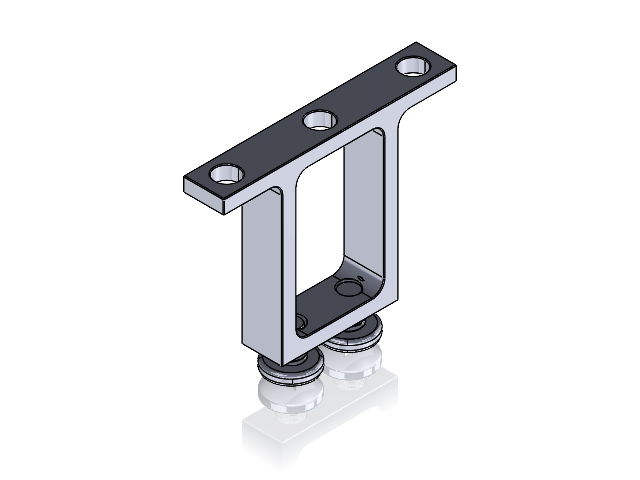
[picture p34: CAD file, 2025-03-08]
CAD Files/V1 AutoBender FIles/bender/servo_horz_mount.SLDASM
1804-0032-0001.STEP
M4 x 5mm zinc plated pan head screw_92005A212.STEP x 2

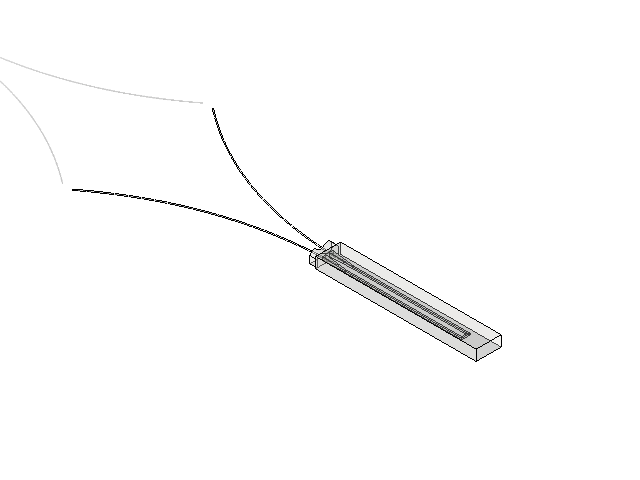
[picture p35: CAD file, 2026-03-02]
CAD Files/sensor fab/strain sensor assembly.SLDASM
strain sensor silicone
red wire x 2
basic strain gauge 0p02
silicone glue

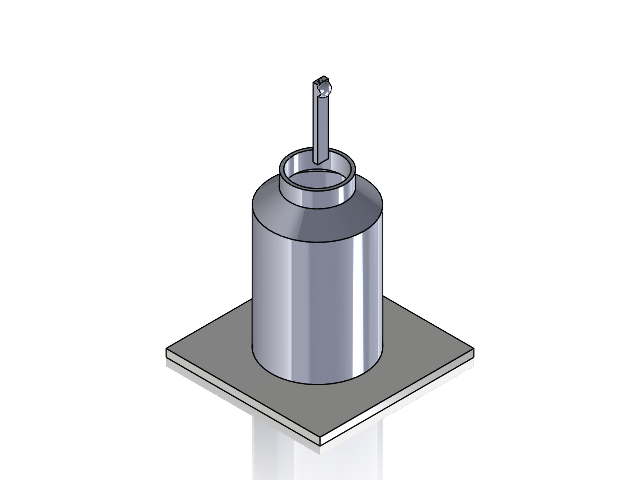
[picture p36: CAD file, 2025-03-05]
CAD Files/sensor fab/acetone dissolve.SLDASM
acetone bottle
acetone
base plate
strain sensor silicone
basic strain gauge 0p02

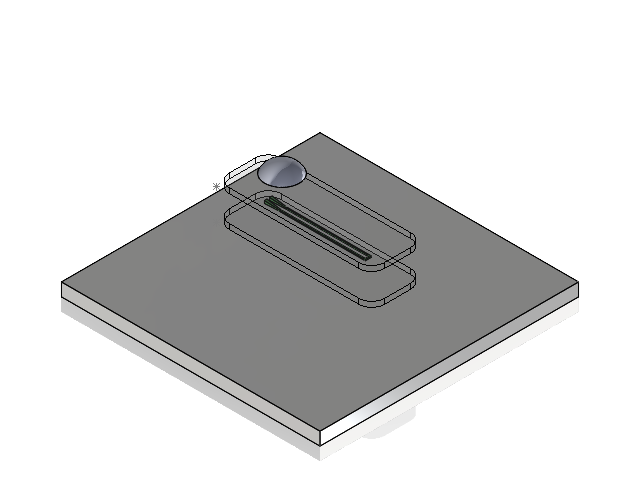
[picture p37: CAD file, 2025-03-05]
CAD Files/sensor fab/sensor fab.SLDASM
base plate
bottom ecoflex layer x 2
basic strain gauge 0p02
bubble

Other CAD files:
CAD Files/tom sensor assembly/Harness_11-Hand with sensors.SLDASM
CAD Files/tom sensor assembly/Harness_13-Hand with sensors.SLDASM
CAD Files/tom sensor assembly/Harness_10-Hand with sensors.SLDASM
CAD Files/tom sensor assembly/Harness_7-Hand with sensors.SLDASM
CAD Files/tom sensor assembly/Harness_4-Hand with sensors.SLDASM
CAD Files/tom sensor assembly/Harness_9-Hand with sensors.SLDASM
CAD Files/tom sensor assembly/Cable_8-Hand with sensors.SLDASM
CAD Files/Sample Holder CNC/plate 1/0p03_total_thickness.ipt
CAD Files/Sample Holder CNC/plate 1/Assembly1.iam
CAD Files/Sample Holder CNC/plate 1/OldVersions/0p03_total_thickness.0005.ipt
CAD Files/Sample Holder CNC/plate 1/OldVersions/Assembly1.0001.iam
CAD Files/V1 AutoBender FIles/Adafruit MCP3421 ADC/2 screw terminal.SLDPRT
CAD Files/V1 AutoBender FIles/Adafruit MCP3421 ADC/Adafruit MCP3421 ADC.SLDASM
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

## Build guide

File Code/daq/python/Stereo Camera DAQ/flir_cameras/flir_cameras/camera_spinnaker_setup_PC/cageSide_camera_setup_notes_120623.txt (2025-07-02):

Notes for camera synch debugging.
12/6/23

SpinView
    Open SpinView
    Assure correct settings.
    Hit "Play" button for both cameras.

    Regarding correct settings:
        Camera settings should be loading from a saved configuration.
        But, key debugging settings that may be wrong that can cause issues:
            Menu: Image Format
                Setting: Pixel Format
                Setting: Frame Width/Height
                    (incorrectly large frames lead to bandwidths that are too high to be saved, leading to dropped frames)
            Menu: GPIO
                Settings: All trigger settings

Arduino
    If camera script is already the script uploaded to the Arduino:

    Click the "Serial Monitor" icon in the upper right-hand corner.
    Input any key to instigate connection.
    Input key to start set of triggers:
        5 for 2000 triggers
        1 for ongoing triggers
        0 for off

Anaconda Prompt
    Open script
    Hit:
        Set Folder
        Start Recording
    In this state, the program is ready to receive images it is given.
        Those images are initiated by any triggers sent to the cameras (e.g. from Arduino script, etc.)

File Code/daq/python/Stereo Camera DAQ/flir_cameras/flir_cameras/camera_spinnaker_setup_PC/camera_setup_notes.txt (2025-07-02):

Notes for setting up top and side cameras for 2017 rig; 

Top camera: ends in 71; SECONDARY
Side camera: ends in 98; PRIMARY 

Hardware trigger setups; https://www.flir.com/support-center/iis/machine-vision/application-note/configuring-synchronized-capture-with-multiple-cameras/

Top camera params: 
Image format: 
	1300 x 700 
	offset x: 500
	offset y: 150
	Pixel format: YCbCr411_8

GPIO: 
	Trigger Mode: on
	Trigger source: Line 3
	Trigger overlap: Read out

Side camera params: 
Image format: 
	1300 x 700 
	offset x: 300
	offset y: 300
	Pixel format: YCbCr411_8

GPIO: 
	Trigger Mode: on
	Trigger source: Line 3
	Trigger overlap: Read out
	Line selector: Line 1
	Line Mode: Output
	3.3V Enable: On; 

Both: 
Acquisition Mode: Continuous

Settings: 
	Exposure Auto: Off
	Exposure Time: 9997us (side camera)
	Exposure Time: 5007us (top camera) 

	Gain Auto: Off
	Gain 4.1 dB

	Gamma Enable: ON 
	Gamma 0.8

	Balance White Auto: Off; 

Chunk Data Control: 
	Chunk Mode Active: On; 
	Chunk Selector: Image Timestamp / Frame ID 
	Chunk Enable: On;

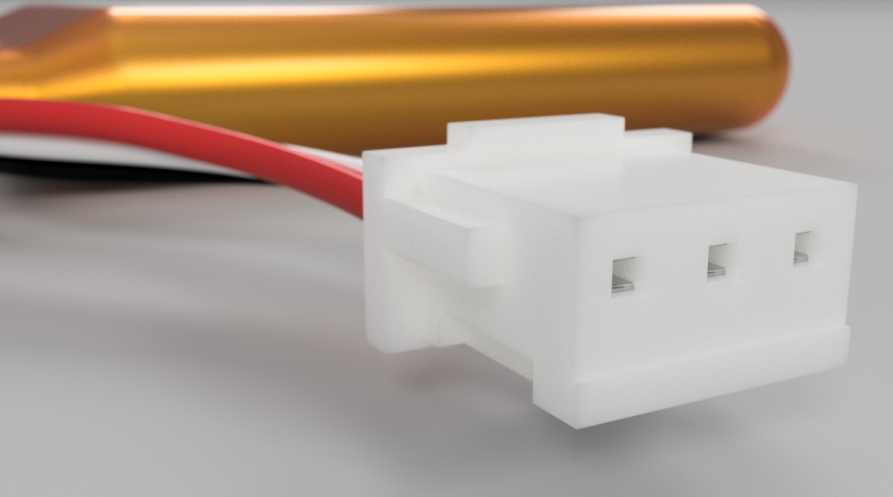
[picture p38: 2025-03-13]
CAD Files/tom sensor assembly/Renders/Battery 4.png

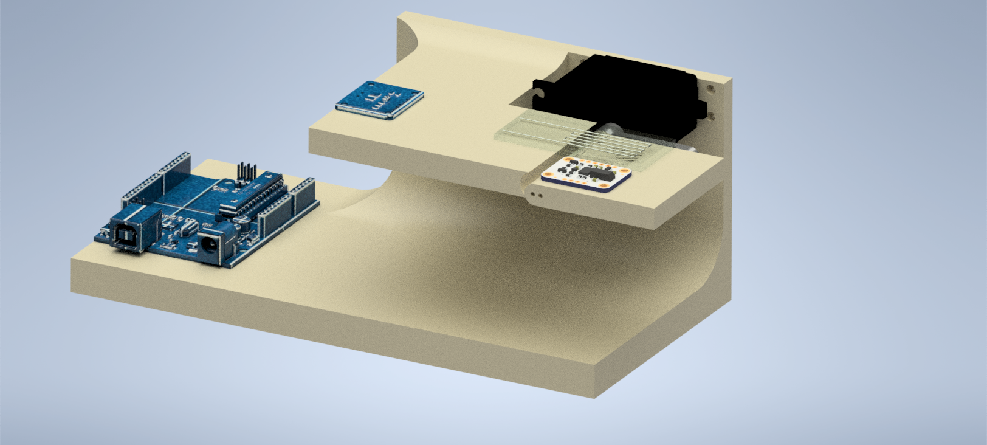
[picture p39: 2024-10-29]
CAD Files/Images and VIdeos/Assembly 2.png

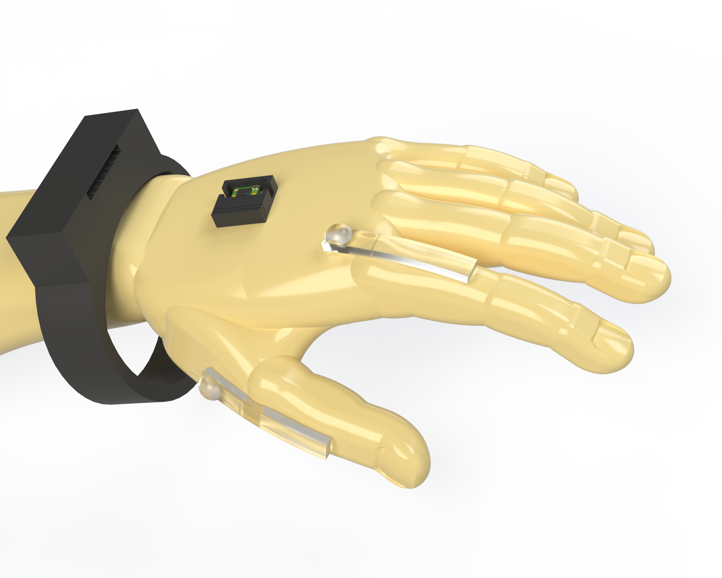
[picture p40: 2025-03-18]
CAD Files/tom sensor assembly/new hand w sensors/new hand w sensors.png

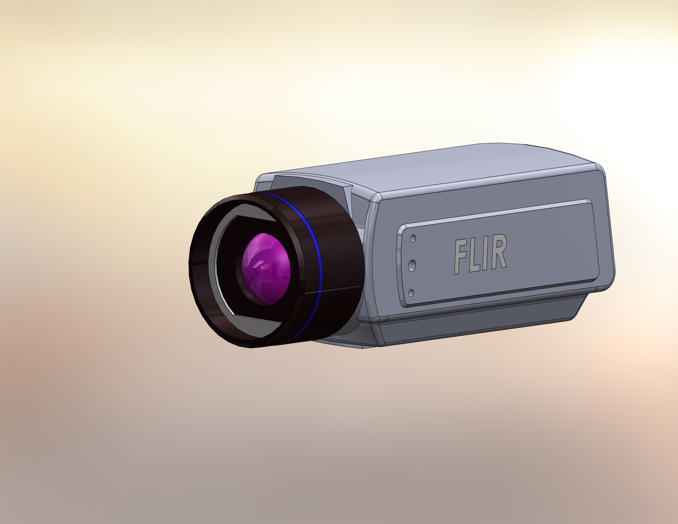
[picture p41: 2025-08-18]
CAD Files/tom sensor assembly/FLIR A615.JPG

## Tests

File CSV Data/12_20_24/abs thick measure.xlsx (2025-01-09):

0.15 mm speed | Th 1 | Th 2 | Th 3 | Average | Std
1 | 0.0175 | 0.017 | 0.0165 | 0.01711666667 | 0.0004219662967
2 | 0.0165 | 0.0165 | 0.017
3 | 0.0165 | 0.017 | 0.016
4 | 0.0175 | 0.0175 | 0.017
5 | 0.017 | 0.018 | 0.017
6 | 0.0175 | 0.0175 | 0.017
7 | 0.0175 | 0.0175 | 0.0175
8 | 0.017 | 0.0175 | 0.017
9 | 0.017 | 0.017 | 0.0175
10 | 0.017 | 0.017 | 0.0175
0.15 mm structural
1 | 0.018 | 0.0175 | 0.0175
2 | 0.017 | 0.017 | 0.0175
3 | 0.017 | 0.018 | 0.017
0.2 mm speed
 | 0.2 | 0.2 | 0.21
 | 0.2 | 0.2 | 0.2
 | 0.21 | 0.21 | 0.21
 | 0.021 | 0.022 | 0.021
 | 0.022 | 0.021 | 0.02
 | 0.02 | 0.02 | 0.02
 | 0.021 | 0.02 | 0.02
 | 0.02 | 0.02 | 0.02
 | 0.02 | 0.02 | 0.02
 | 0.02 | 0.02 | 0.02
0.1 mm Fast Detail
 | 0.015 | 0.014
 | 0.017 | 0.018
 | 0.016 | 0.016
 | 0.018 | 0.017
 | 0.017 | 0.018
 | 0.016 | 0.016
 | 0.017 | 0.016
 | 0.017 | 0.017
 | 0.016 | 0.016
 | 0.017 | 0.017
 | 0.018 | 0.018

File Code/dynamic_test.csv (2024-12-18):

Theoretical Angle (deg) | IMU Angle (deg) | ADC Value | Rotary Encoder
100.0 | 100.0 | 100.0 | 100.0
100.0 | 100.0 | 100.0 | 100.0
70.0 | -55.75 | -32768.0 | 432.0
70.0 | -25.0 | -32768.0 | 508.0
10.0 | -51.88 | -32768.0 | 271.0
10.0 | -84.5 | -32768.0 | 244.0
10.0 | -87.69 | -32768.0 | 244.0
10.0 | -87.69 | -32768.0 | 244.0
10.0 | -87.62 | -32768.0 | 244.0
70.0 | -42.25 | -32768.0 | 476.0
70.0 | -14.06 | -32768.0 | 515.0
70.0 | -6.25 | -32768.0 | 515.0
70.0 | -6.19 | -32768.0 | 515.0
70.0 | -6.0 | -32768.0 | 515.0
10.0 | -54.94 | -32768.0 | 269.0
10.0 | -85.44 | -32768.0 | 246.0
10.0 | -88.37 | -32768.0 | 244.0
10.0 | -88.37 | -32768.0 | 244.0
10.0 | -88.0 | -32768.0 | 244.0
70.0 | -43.75 | -32768.0 | 469.0
70.0 | -14.44 | -32768.0 | 515.0
70.0 | -3.44 | -32768.0 | 515.0
70.0 | -3.5 | -32768.0 | 515.0
70.0 | -3.63 | -32768.0 | 515.0
10.0 | -51.38 | -32768.0 | 276.0
10.0 | -82.62 | -32768.0 | 245.0
10.0 | -87.75 | -32768.0 | 245.0
10.0 | -87.69 | -32768.0 | 244.0
10.0 | -87.37 | -32768.0 | 245.0

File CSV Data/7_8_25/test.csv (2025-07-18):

Tue  Jul 8  2025 1:31 PM
Channel 0

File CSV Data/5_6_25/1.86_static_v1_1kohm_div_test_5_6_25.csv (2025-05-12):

Theoretical Angle (deg) | IMU Angle (deg) | ADC Value | Rotary Encoder
70.0 | -4.75 | -27748.0 | 516.0
70.0 | -4.63 | -27753.0 | 515.0
70.0 | -4.56 | -27750.0 | 516.0
70.0 | -4.5 | -27802.0 | 516.0
70.0 | -4.44 | -27788.0 | 515.0
70.0 | -4.38 | -27674.0 | 516.0
70.0 | -4.31 | -27671.0 | 515.0
70.0 | -4.31 | -27662.0 | 515.0
70.0 | -4.31 | -27675.0 | 516.0
70.0 | -4.31 | -27670.0 | 516.0
70.0 | -4.31 | -27676.0 | 515.0
70.0 | -4.31 | -27768.0 | 515.0
70.0 | -4.31 | -27807.0 | 515.0
70.0 | -4.31 | -27808.0 | 515.0
70.0 | -4.31 | -27817.0 | 516.0
70.0 | -4.31 | -27759.0 | 516.0
70.0 | -4.31 | -27665.0 | 515.0
70.0 | -4.31 | -27671.0 | 516.0
70.0 | -4.31 | -27681.0 | 515.0
70.0 | -4.31 | -27693.0 | 515.0
70.0 | -4.31 | -27690.0 | 515.0
70.0 | -4.31 | -27680.0 | 515.0
70.0 | -4.31 | -27670.0 | 515.0
70.0 | -4.31 | -27824.0 | 515.0
70.0 | -4.31 | -27842.0 | 515.0
70.0 | -4.31 | -27817.0 | 516.0
70.0 | -4.31 | -27801.0 | 515.0
70.0 | -4.31 | -27664.0 | 516.0
70.0 | -4.31 | -27707.0 | 515.0
70.0 | -4.31 | -27700.0 | 515.0
70.0 | -4.31 | -27682.0 | 515.0
70.0 | -4.31 | -27684.0 | 516.0
70.0 | -4.31 | -27687.0 | 515.0
70.0 | -4.31 | -27715.0 | 520.0
70.0 | -2.94 | -27787.0 | 519.0
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

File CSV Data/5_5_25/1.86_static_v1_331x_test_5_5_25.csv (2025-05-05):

Theoretical Angle (deg) | IMU Angle (deg) | ADC Value | Rotary Encoder
100.0 | 100.0 | 100.0 | 100.0
100.0 | 100.0 | 100.0 | 100.0
70.0 | -2.88 | -17343.0 | 512.0
70.0 | -3.0 | -17370.0 | 511.0
70.0 | -3.13 | -17398.0 | 512.0
70.0 | -3.25 | -17425.0 | 511.0
70.0 | -3.31 | -17437.0 | 511.0
70.0 | -3.38 | -17468.0 | 512.0
70.0 | -3.44 | -17435.0 | 512.0
70.0 | -3.5 | -17498.0 | 512.0
70.0 | -3.56 | -17495.0 | 510.0
70.0 | -3.56 | -17493.0 | 512.0
70.0 | -3.56 | -17539.0 | 512.0
70.0 | -3.56 | -17551.0 | 512.0
70.0 | -3.56 | -17524.0 | 511.0
70.0 | -3.56 | -17527.0 | 512.0
70.0 | -3.56 | -17549.0 | 512.0
70.0 | -3.56 | -17556.0 | 512.0
70.0 | -3.56 | -17548.0 | 511.0
70.0 | -3.56 | -17509.0 | 511.0
70.0 | -3.56 | -17567.0 | 512.0
70.0 | -3.56 | -17575.0 | 512.0
70.0 | -3.56 | -17565.0 | 511.0
70.0 | -3.56 | -17560.0 | 512.0
70.0 | -3.56 | -17555.0 | 512.0
70.0 | -3.56 | -17543.0 | 511.0
70.0 | -3.56 | -17511.0 | 512.0
70.0 | -3.56 | -17555.0 | 512.0
70.0 | -3.56 | -17566.0 | 512.0
70.0 | -3.56 | -17515.0 | 511.0
70.0 | -3.56 | -17549.0 | 513.0
70.0 | -3.56 | -17543.0 | 512.0
70.0 | -3.56 | -17542.0 | 512.0
60.0 | -16.19 | -15912.0 | 474.0
60.0 | -16.19 | -15888.0 | 474.0
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

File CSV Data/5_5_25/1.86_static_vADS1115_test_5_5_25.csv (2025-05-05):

Theoretical Angle (deg) | IMU Angle (deg) | ADC Value | Rotary Encoder
70.0 | -4.44 | -15766.0 | 513.0
70.0 | -4.38 | -15767.0 | 513.0
70.0 | -4.31 | -15765.0 | 513.0
70.0 | -4.31 | -15772.0 | 514.0
70.0 | -4.25 | -15904.0 | 514.0
70.0 | -4.25 | -15931.0 | 514.0
70.0 | -4.19 | -15925.0 | 514.0
70.0 | -4.19 | -15944.0 | 514.0
70.0 | -4.19 | -15979.0 | 514.0
70.0 | -4.19 | -15921.0 | 514.0
70.0 | -4.19 | -15818.0 | 513.0
70.0 | -4.19 | -15814.0 | 514.0
70.0 | -4.19 | -15857.0 | 513.0
70.0 | -4.19 | -15849.0 | 514.0
70.0 | -4.19 | -15838.0 | 514.0
70.0 | -4.19 | -15829.0 | 514.0
70.0 | -4.19 | -15963.0 | 514.0
70.0 | -4.19 | -16095.0 | 514.0
70.0 | -4.19 | -16034.0 | 514.0
70.0 | -4.19 | -16006.0 | 513.0
70.0 | -4.19 | -15933.0 | 514.0
70.0 | -4.06 | -15964.0 | 514.0
70.0 | -4.06 | -15926.0 | 514.0
70.0 | -4.06 | -15904.0 | 514.0
70.0 | -4.06 | -15905.0 | 514.0
70.0 | -4.06 | -15887.0 | 514.0
70.0 | -4.06 | -15937.0 | 514.0
70.0 | -4.06 | -15914.0 | 514.0
70.0 | -4.06 | -16017.0 | 514.0
70.0 | -4.06 | -16001.0 | 514.0
70.0 | -4.06 | -15994.0 | 514.0
70.0 | -4.06 | -15972.0 | 514.0
70.0 | -4.06 | -15885.0 | 514.0
70.0 | -4.06 | -15875.0 | 514.0
70.0 | -4.06 | -15918.0 | 514.0
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

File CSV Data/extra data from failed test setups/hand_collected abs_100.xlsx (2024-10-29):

angle | voltage
90 | 14.4
75 | 12.2
60 | 10.4
45 | 9
30 | 7.7
15 | 6.6
0 | 5.6
90 | 14.4
75 | 12.1
60 | 10.3
45 | 8.7
30 | 7.5
15 | 6.5
0 | NaN
90 | NaN
75 | 12.3
60 | 10.5
45 | 9.1
30 | 7.5
15 | 6.7
0 | 5.7
90 | 14.7
75 | 12.2
60 | 10.4
45 | 8.9
30 | 7.6
15 | 6.5
0
90
75 | 12.5
60 | 10.8
45 | 9.4
30 | 8.2
15 | 6.9
0 | 5.8
90 | 14.9
75 | 12.4
60 | 10.6
45 | 9.1
30 | 7.8
15 | 6.7
0 | NaN
90 | NaN
75 | 12.7
60 | 11
45 | 9.7
30 | 8.5
15 | 7.1
0 | 6
90 | 14.8
75 | 12.3
60 | 10.7
45 | 9.4
30 | 8.1
15 | 6.6
0 | NaN
90 | NaN
75 | 12.7
60 | 11.1
45 | 9.8
30 | 8.7
15 | 7.3
0 | 6.1

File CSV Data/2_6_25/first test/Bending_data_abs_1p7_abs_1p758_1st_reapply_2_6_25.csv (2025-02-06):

Theoretical Angle (deg) | IMU Angle (deg) | ADC Value | Rotary Encoder
92.0 | 4.44 | -92.0 | 516.0
70.0 | -4.44 | -92.0 | 516.0
70.0 | -4.44 | -92.0 | 516.0
70.0 | -4.44 | -92.0 | 516.0
70.0 | -4.44 | -92.0 | 516.0
70.0 | -4.44 | -92.0 | 516.0
70.0 | -4.44 | -92.0 | 516.0
100.0 | 100.0 | 100.0 | 100.0
70.0 | -3.44 | -92.0 | 515.0
70.0 | -3.63 | -92.0 | 515.0
70.0 | -3.75 | -92.0 | 516.0
70.0 | -3.88 | -92.0 | 515.0
70.0 | -3.94 | -92.0 | 516.0
70.0 | -4.06 | -92.0 | 516.0
70.0 | -4.13 | -92.0 | 516.0
70.0 | -4.19 | -92.0 | 516.0
70.0 | -4.25 | -92.0 | 515.0
70.0 | -4.31 | -92.0 | 516.0
70.0 | -4.38 | -92.0 | 516.0
70.0 | -4.38 | -92.0 | 516.0
70.0 | -4.38 | -92.0 | 516.0
70.0 | -4.38 | -92.0 | 516.0
70.0 | -4.38 | -92.0 | 516.0
70.0 | -4.38 | -92.0 | 515.0
70.0 | -4.38 | -92.0 | 516.0
70.0 | -4.38 | -92.0 | 515.0
70.0 | -4.38 | -92.0 | 516.0
70.0 | -4.38 | -92.0 | 516.0
70.0 | -4.38 | -92.0 | 516.0
70.0 | -4.38 | -92.0 | 516.0
70.0 | -4.38 | -92.0 | 516.0
70.0 | -4.38 | -92.0 | 515.0
70.0 | -4.38 | -92.0 | 516.0
70.0 | -4.38 | -92.0 | 516.0
70.0 | -4.38 | -92.0 | 516.0
70.0 | -4.38 | -92.0 | 516.0
70.0 | -4.38 | -92.0 | 516.0
70.0 | -4.38 | -92.0 | 516.0
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

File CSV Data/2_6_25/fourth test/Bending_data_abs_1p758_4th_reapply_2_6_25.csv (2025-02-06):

Theoretical Angle (deg) | IMU Angle (deg) | ADC Value | Rotary Encoder
100.0 | 100.0 | 100.0 | 100.0
70.0 | -3.44 | -107.0 | 516.0
70.0 | -3.56 | -107.0 | 515.0
70.0 | -3.75 | -107.0 | 515.0
70.0 | -3.81 | -107.0 | 516.0
70.0 | -3.94 | -107.0 | 516.0
70.0 | -4.0 | -107.0 | 515.0
70.0 | -4.0 | -107.0 | 515.0
70.0 | -4.13 | -107.0 | 515.0
70.0 | -4.19 | -107.0 | 516.0
70.0 | -4.25 | -107.0 | 515.0
70.0 | -4.25 | -107.0 | 515.0
70.0 | -4.25 | -107.0 | 515.0
70.0 | -4.25 | -107.0 | 515.0
70.0 | -4.25 | -107.0 | 515.0
70.0 | -4.25 | -107.0 | 515.0
70.0 | -4.25 | -107.0 | 516.0
70.0 | -4.25 | -107.0 | 516.0
70.0 | -4.25 | -107.0 | 515.0
70.0 | -4.25 | -107.0 | 516.0
70.0 | -4.25 | -107.0 | 516.0
70.0 | -4.25 | -107.0 | 516.0
70.0 | -4.25 | -107.0 | 515.0
70.0 | -4.25 | -107.0 | 515.0
70.0 | -4.25 | -107.0 | 515.0
70.0 | -4.25 | -107.0 | 515.0
70.0 | -4.25 | -107.0 | 515.0
70.0 | -4.25 | -107.0 | 516.0
70.0 | -4.25 | -107.0 | 516.0
70.0 | -4.25 | -107.0 | 516.0
70.0 | -4.25 | -107.0 | 515.0
70.0 | -4.25 | -107.0 | 516.0
70.0 | -4.25 | -107.0 | 515.0
70.0 | -4.25 | -107.0 | 515.0
70.0 | -4.25 | -107.0 | 515.0
70.0 | -4.25 | -107.0 | 515.0
70.0 | -4.25 | -107.0 | 516.0
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

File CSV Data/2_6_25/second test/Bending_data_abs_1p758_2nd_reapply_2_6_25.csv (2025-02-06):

Theoretical Angle (deg) | IMU Angle (deg) | ADC Value | Rotary Encoder
100.0 | 100.0 | 100.0 | 100.0
70.0 | -3.88 | -89.0 | 515.0
70.0 | -4.0 | -89.0 | 515.0
70.0 | -4.06 | -89.0 | 521.0
70.0 | -2.25 | -89.0 | 520.0
70.0 | -2.56 | -88.0 | 520.0
70.0 | -2.63 | -89.0 | 520.0
70.0 | -2.69 | -89.0 | 520.0
70.0 | -2.69 | -88.0 | 520.0
70.0 | -2.75 | -88.0 | 521.0
70.0 | -2.81 | -88.0 | 521.0
70.0 | -2.81 | -88.0 | 520.0
70.0 | -2.88 | -88.0 | 520.0
70.0 | -2.88 | -88.0 | 520.0
70.0 | -2.88 | -88.0 | 523.0
70.0 | -2.44 | -88.0 | 520.0
70.0 | -3.0 | -88.0 | 520.0
70.0 | -3.0 | -88.0 | 520.0
70.0 | -3.0 | -88.0 | 521.0
70.0 | -3.0 | -88.0 | 521.0
70.0 | -3.0 | -88.0 | 521.0
70.0 | -3.0 | -88.0 | 520.0
70.0 | -3.0 | -88.0 | 521.0
70.0 | -3.0 | -88.0 | 520.0
70.0 | -3.0 | -89.0 | 521.0
70.0 | -3.0 | -88.0 | 521.0
70.0 | -3.0 | -88.0 | 520.0
70.0 | -3.0 | -88.0 | 521.0
70.0 | -3.0 | -88.0 | 521.0
70.0 | -3.0 | -88.0 | 521.0
70.0 | -3.0 | -88.0 | 521.0
70.0 | -3.0 | -88.0 | 521.0
70.0 | -3.0 | -88.0 | 520.0
70.0 | -3.0 | -88.0 | 520.0
70.0 | -3.0 | -88.0 | 520.0
70.0 | -3.0 | -88.0 | 521.0
70.0 | -3.0 | -88.0 | 520.0
70.0 | -3.0 | -88.0 | 521.0
60.0 | -16.94 | -93.0 | 478.0
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

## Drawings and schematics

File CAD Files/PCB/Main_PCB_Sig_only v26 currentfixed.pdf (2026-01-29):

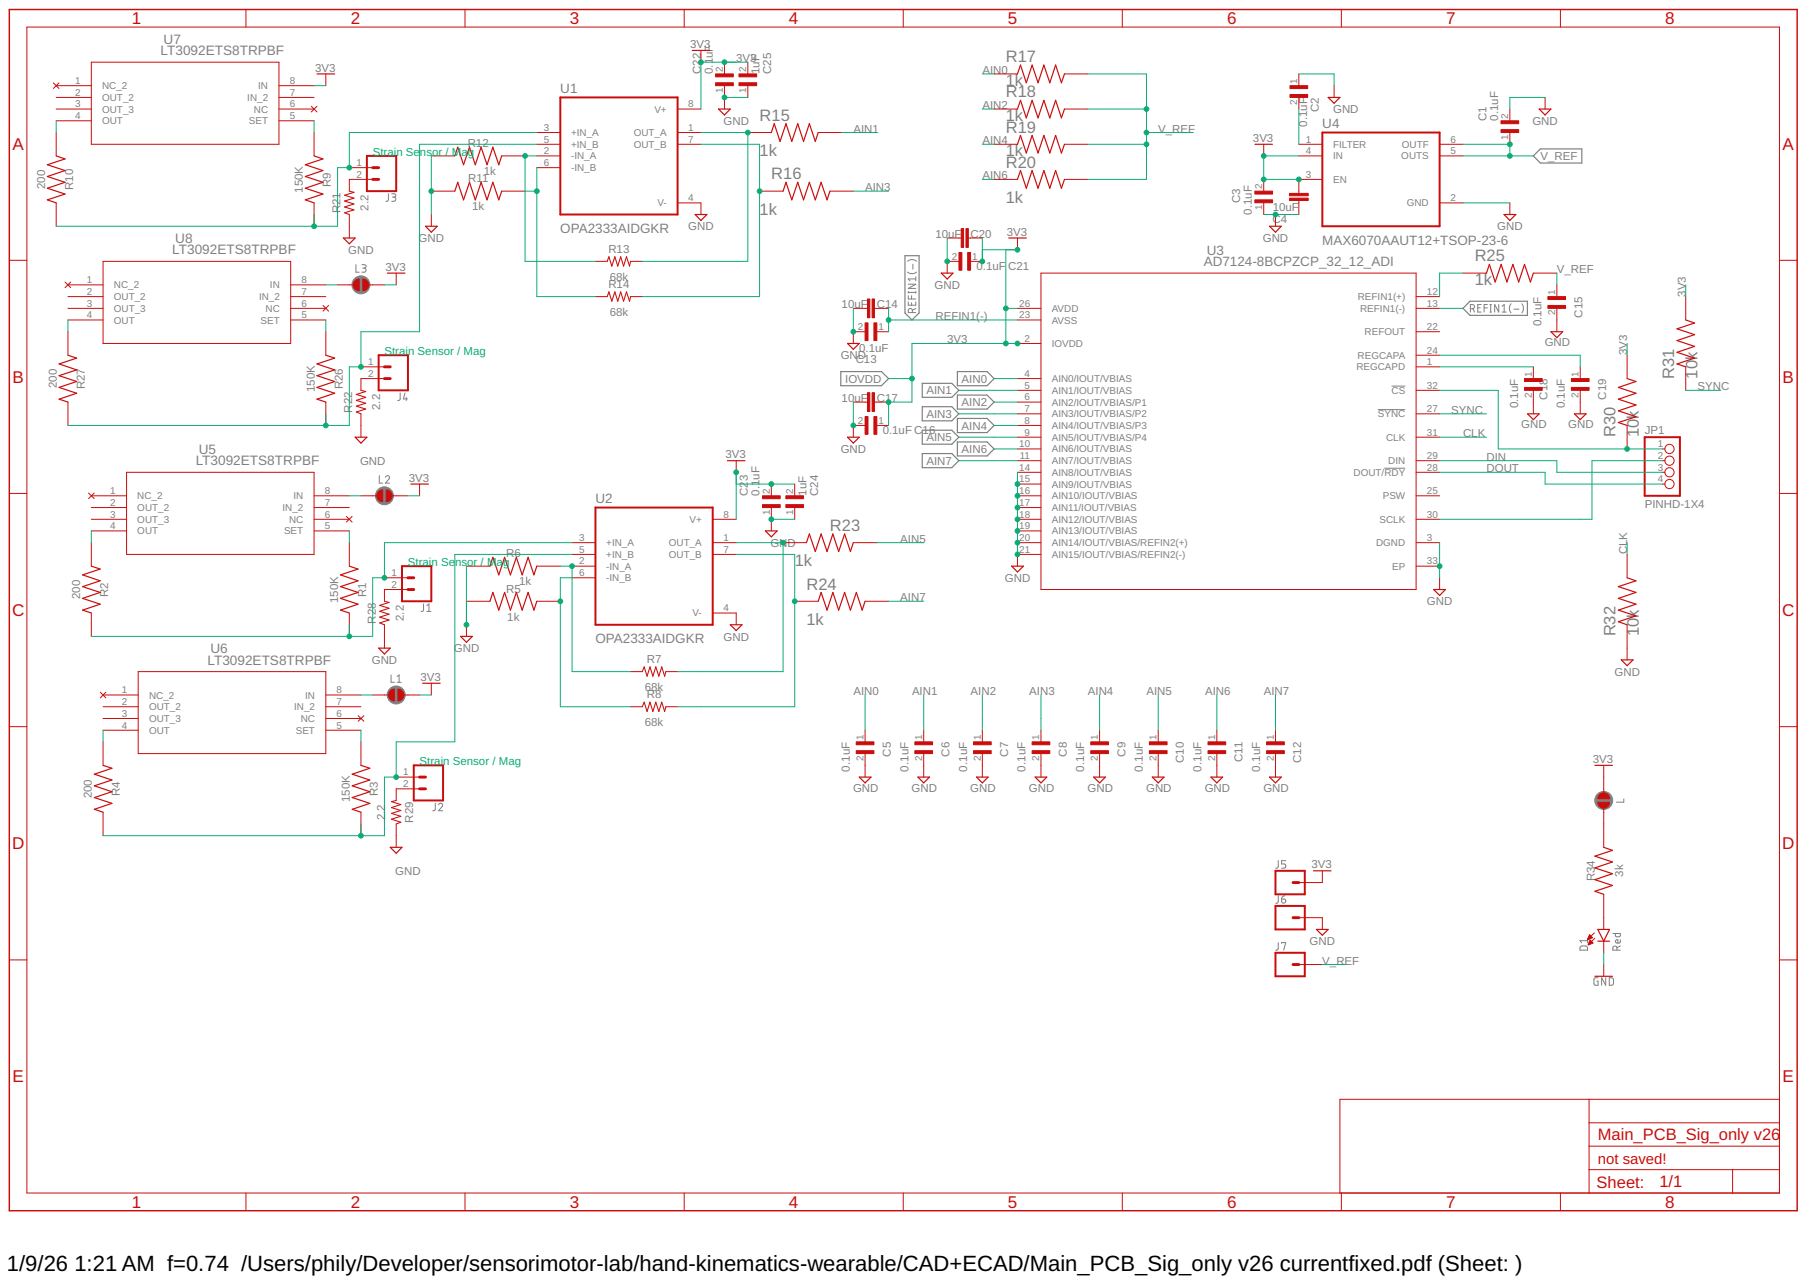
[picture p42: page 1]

1/9/26 1:21 AM f=0.74 /Users/phily/Developer/sensorimotor-lab/hand-kinematics-wearable/CAD+ECAD/Main_PCB_Sig_only v26 currentfixed.pdf (Sheet: )

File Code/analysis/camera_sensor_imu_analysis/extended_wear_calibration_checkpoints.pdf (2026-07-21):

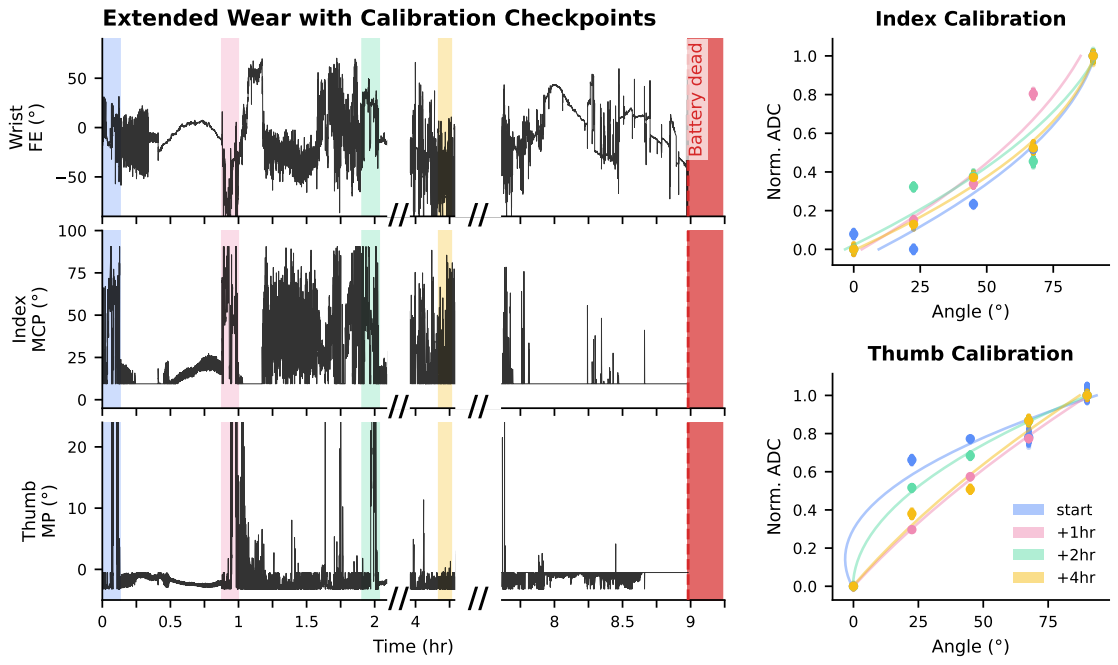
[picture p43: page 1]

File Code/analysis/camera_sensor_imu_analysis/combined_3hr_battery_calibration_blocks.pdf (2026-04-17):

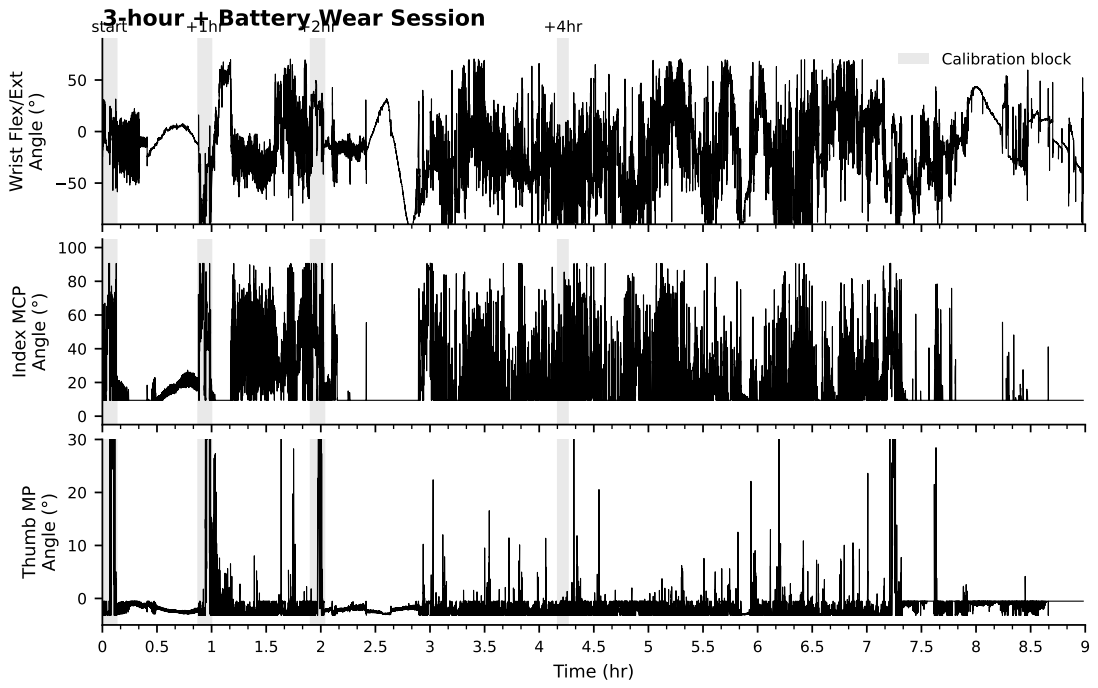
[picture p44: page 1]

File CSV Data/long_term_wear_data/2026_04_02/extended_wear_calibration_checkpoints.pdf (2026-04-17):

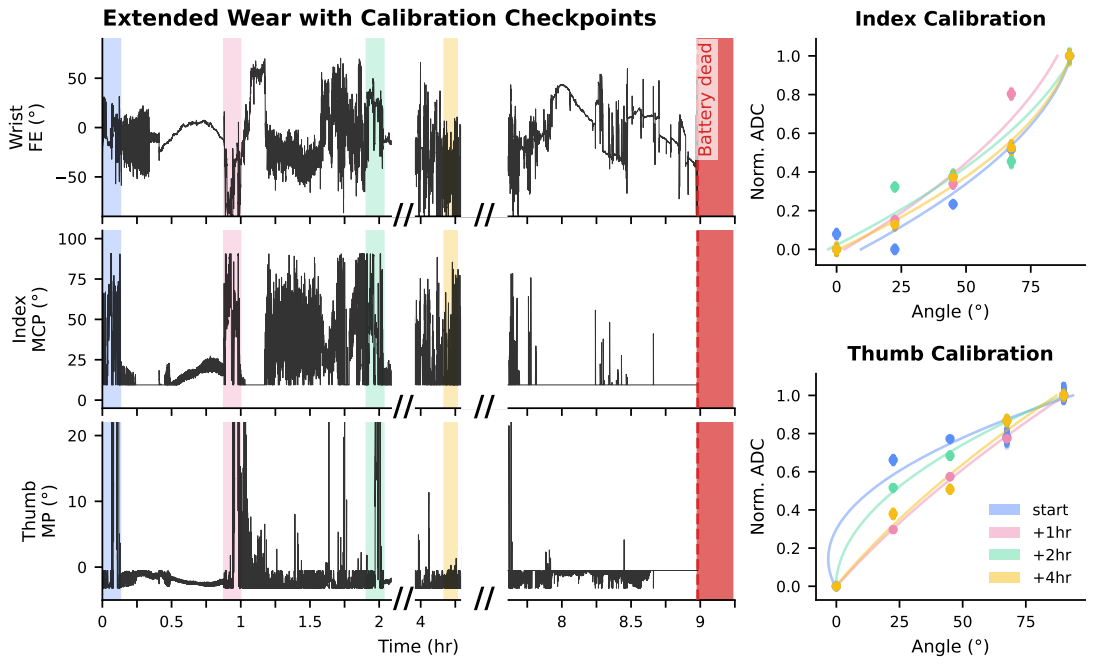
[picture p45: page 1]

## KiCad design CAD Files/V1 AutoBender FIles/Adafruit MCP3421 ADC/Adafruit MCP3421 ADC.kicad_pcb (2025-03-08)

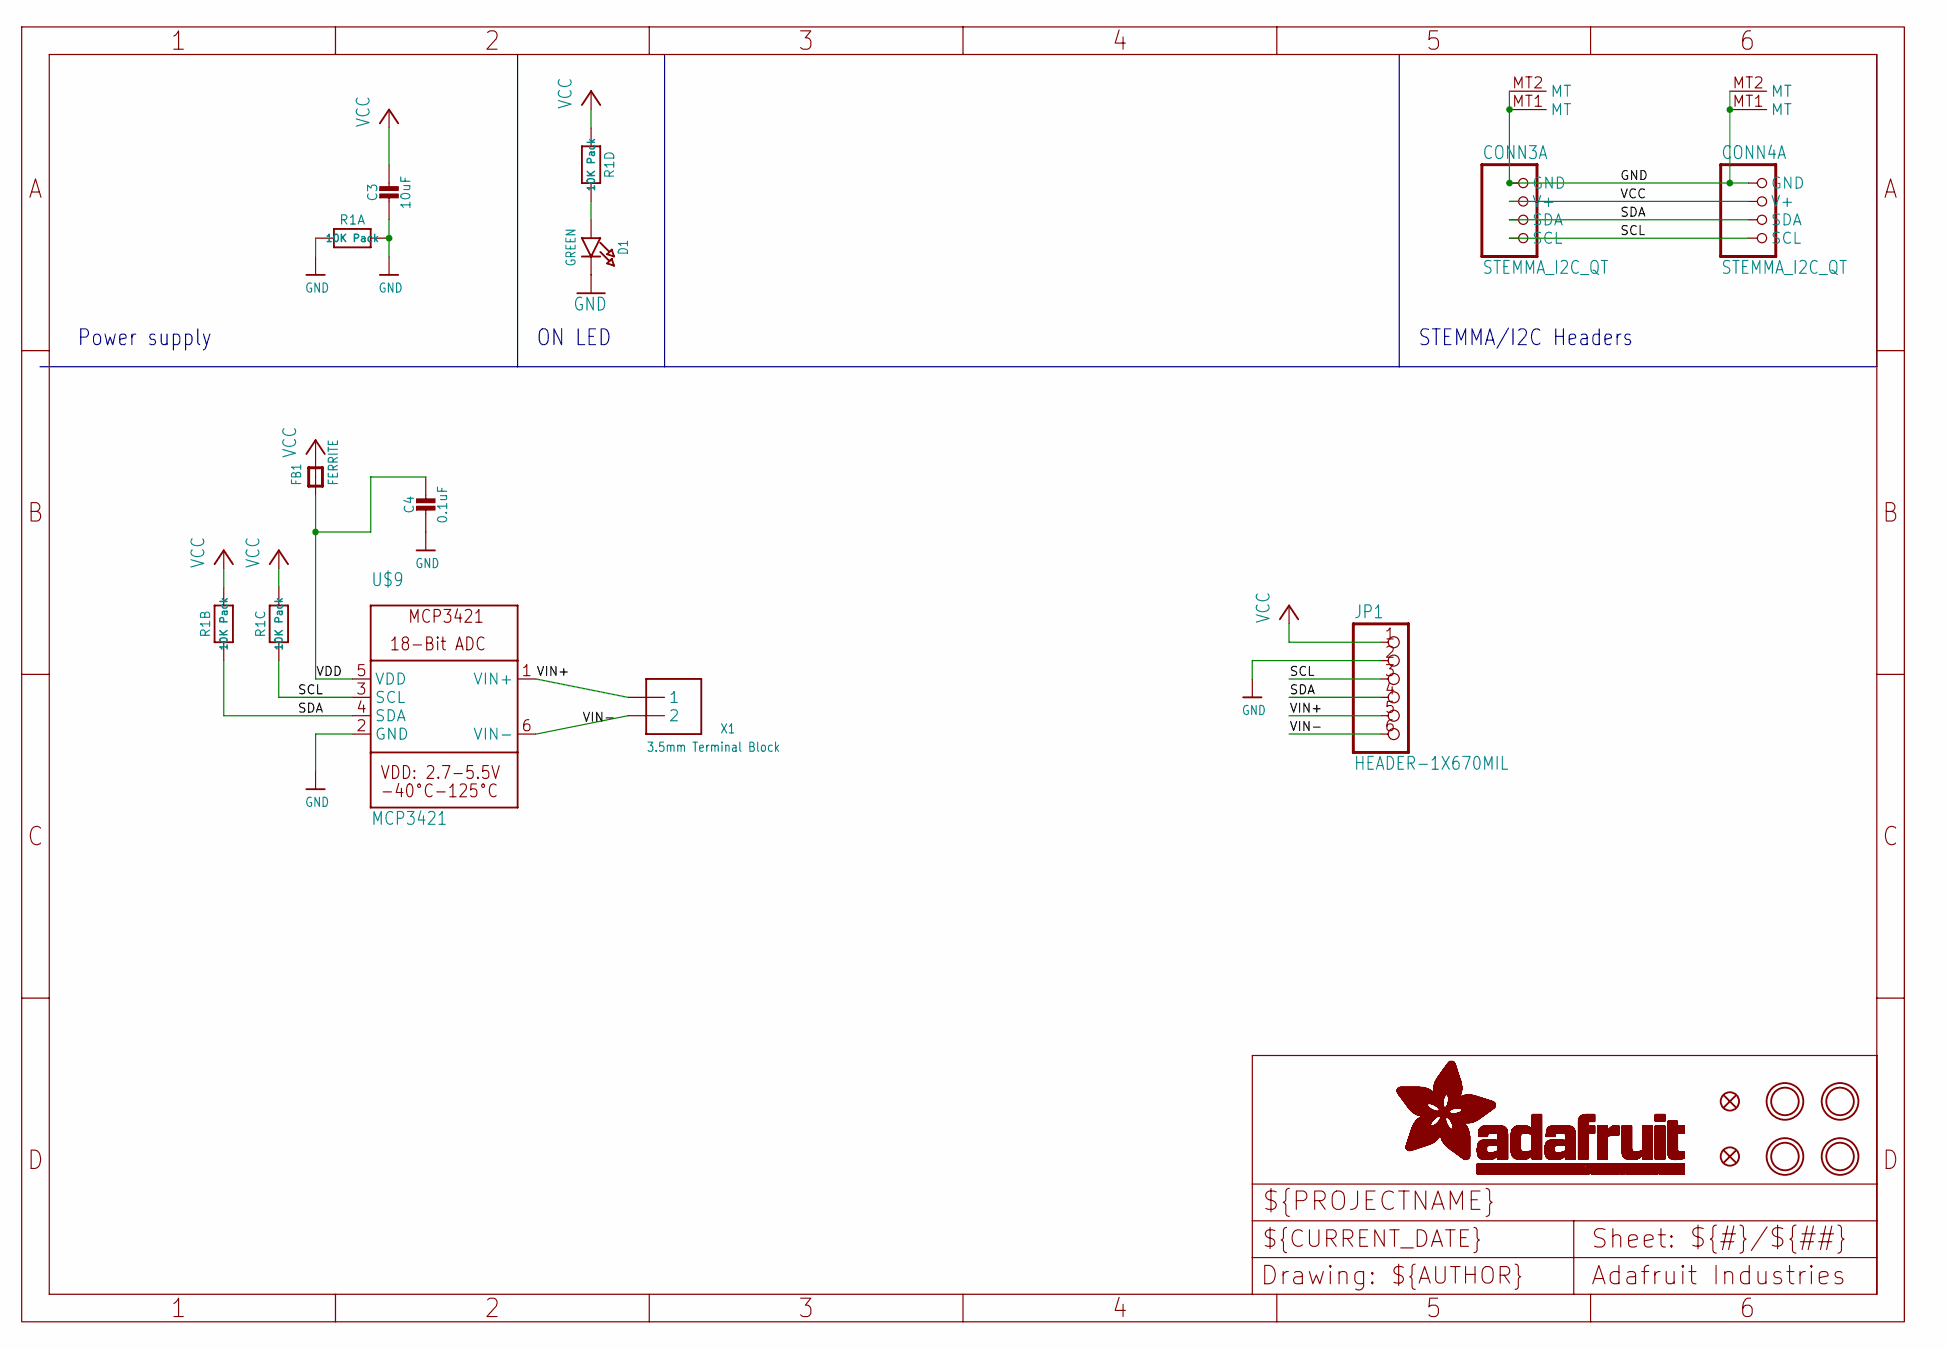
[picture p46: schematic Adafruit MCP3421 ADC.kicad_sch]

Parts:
C3: 10uF; 0805-NO
C4: 0.1uF; 0603-NO
CONN3, CONN4: STEMMA_I2C_QT; JST_SH4
D1: GREEN; CHIPLED_0603_NOOUTLINE
FB1: FERRITE; 0603-NO
FID3, FID4: FIDUCIAL_1MM
JP1: HEADER-1X670MIL; 1X06_ROUND_70
R1: 10K Pack; RESPACK_4X0603
U$9: MCP3421; SOT23-6
U$20, U$21, U$25, U$27: MOUNTINGHOLE2.5; MOUNTINGHOLE_2.5_PLATED
X1: 3.5mm Terminal Block; TERMBLOCK_1X2-3.5MM

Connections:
GND: C3.2, C4.2, CONN3.1 (GND), CONN3.MT1 (MT), CONN3.MT2 (MT), CONN4.1 (GND), CONN4.MT1 (MT), CONN4.MT2 (MT), D1.C, JP1.2, R1.1, R1.8 (2), U$9.2 (GND)
unnamed: D1.A, R1.5 (2)
SCL: CONN3.4 (SCL), CONN4.4 (SCL), JP1.3, R1.3 (1), U$9.3 (SCL)
SDA: CONN3.3 (SDA), CONN4.3 (SDA), JP1.4, R1.2 (1), U$9.4 (SDA)
VCC: C3.1, CONN3.2 (V+), CONN4.2 (V+), FB1.2, JP1.1, R1.4 (1), R1.6 (2), R1.7 (2)
VDD: C4.1, FB1.1, U$9.5 (VDD)
VIN+: JP1.5, U$9.1 (VIN+), X1.1
VIN-: JP1.6, U$9.6 (VIN-), X1.2

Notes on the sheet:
ON LED
STEMMA/I2C Headers
Power supply

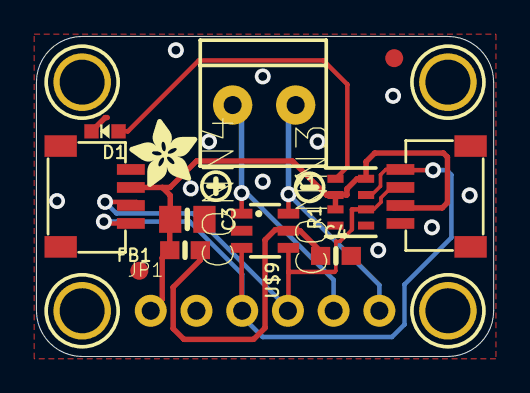
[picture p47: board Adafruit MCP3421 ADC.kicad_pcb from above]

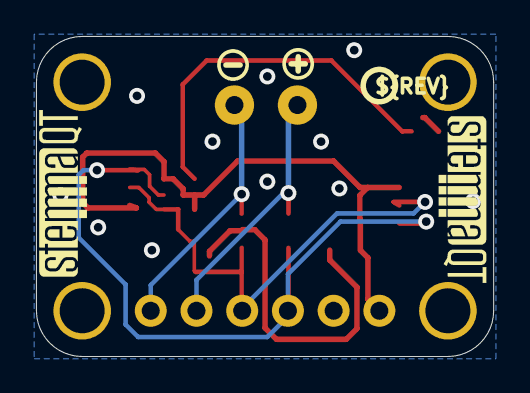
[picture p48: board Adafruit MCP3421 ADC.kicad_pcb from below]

Board: 2 copper layers, 25.4 x 17.8 mm, 37 parts (9 on the bottom side), 8 nets.

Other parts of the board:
PLABEL0: PLABEL0
PLABEL1: PLABEL1
PLABEL2: PLABEL2
PLABEL3: PLABEL3
PLABEL4: PLABEL4
PLABEL5: PLABEL5
PLABEL6: PLABEL6
PLABEL7: PLABEL7
PLABEL8: PLABEL8
PLABEL9: PLABEL9
PLABEL10: PLABEL10
PLABEL11: PLABEL11
PLABEL12: PLABEL12
U$2, U$7: SYMBOL_PLUS
U$4, U$5: SYMBOL_MINUS
U$8: PCBFEAT-REV-040
U$29: ADAFRUIT_3.5MM
U$31, U$32: STEMMAQT

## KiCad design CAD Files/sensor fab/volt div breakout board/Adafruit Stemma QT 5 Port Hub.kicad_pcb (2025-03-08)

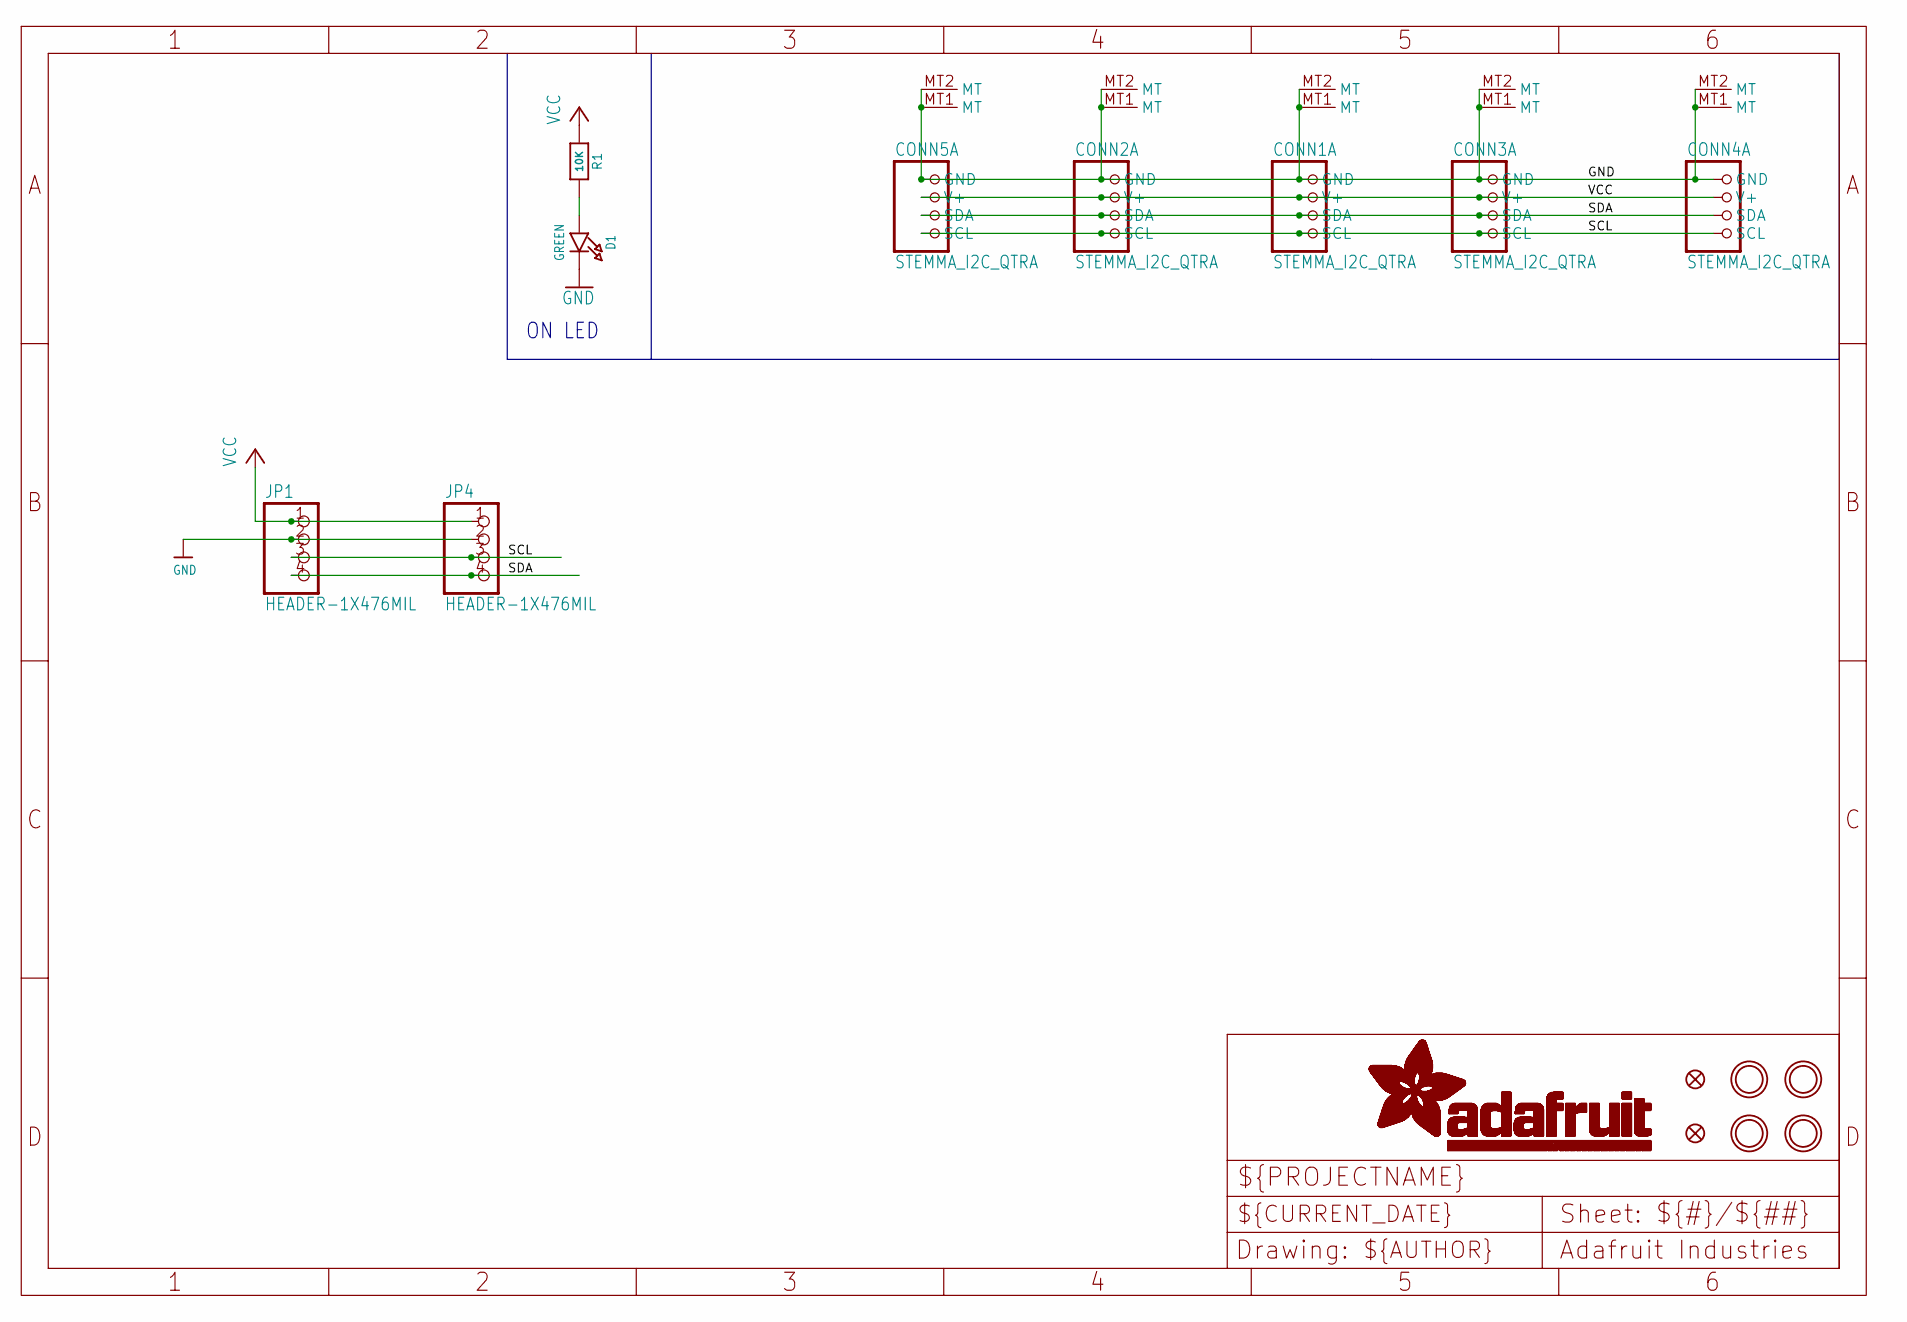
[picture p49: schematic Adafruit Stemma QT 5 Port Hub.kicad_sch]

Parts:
CONN1, CONN2, CONN3, CONN4, CONN5: STEMMA_I2C_QTRA; JST_SH4_RA
D1: GREEN; CHIPLED_0603_NOOUTLINE
FID3, FID4: FIDUCIAL_1MM
JP1, JP4: HEADER-1X476MIL; 1X04_ROUND_76
R1: 10K; 0603-NO
U$1, U$17, U$19, U$21: MOUNTINGHOLE2.5; MOUNTINGHOLE_2.5_PLATED

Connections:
GND: CONN1.1 (GND), CONN1.MT1 (MT), CONN1.MT2 (MT), CONN2.1 (GND), CONN2.MT1 (MT), CONN2.MT2 (MT), CONN3.1 (GND), CONN3.MT1 (MT), CONN3.MT2 (MT), CONN4.1 (GND), CONN4.MT1 (MT), CONN4.MT2 (MT), CONN5.1 (GND), CONN5.MT1 (MT), CONN5.MT2 (MT), D1.C, JP1.2, JP4.2
unnamed: D1.A, R1.2
SCL: CONN1.4 (SCL), CONN2.4 (SCL), CONN3.4 (SCL), CONN4.4 (SCL), CONN5.4 (SCL), JP1.3, JP4.3
SDA: CONN1.3 (SDA), CONN2.3 (SDA), CONN3.3 (SDA), CONN4.3 (SDA), CONN5.3 (SDA), JP1.4, JP4.4
VCC: CONN1.2 (V+), CONN2.2 (V+), CONN3.2 (V+), CONN4.2 (V+), CONN5.2 (V+), JP1.1, JP4.1, R1.1

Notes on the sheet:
ON LED

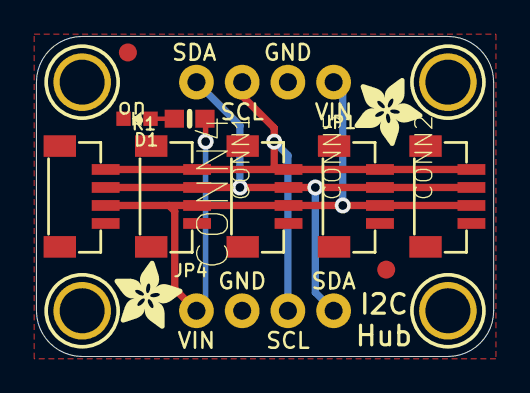
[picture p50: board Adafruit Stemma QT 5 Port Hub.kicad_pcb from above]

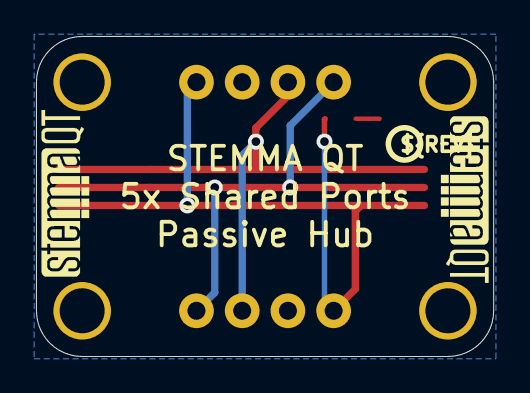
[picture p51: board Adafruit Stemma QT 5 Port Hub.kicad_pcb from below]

Board: 2 copper layers, 25.4 x 17.8 mm, 20 parts (3 on the bottom side), 5 nets.

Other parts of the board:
U$2, U$3: ADAFRUIT_3.5MM
U$25: PCBFEAT-REV-040
U$30, U$31: STEMMAQT

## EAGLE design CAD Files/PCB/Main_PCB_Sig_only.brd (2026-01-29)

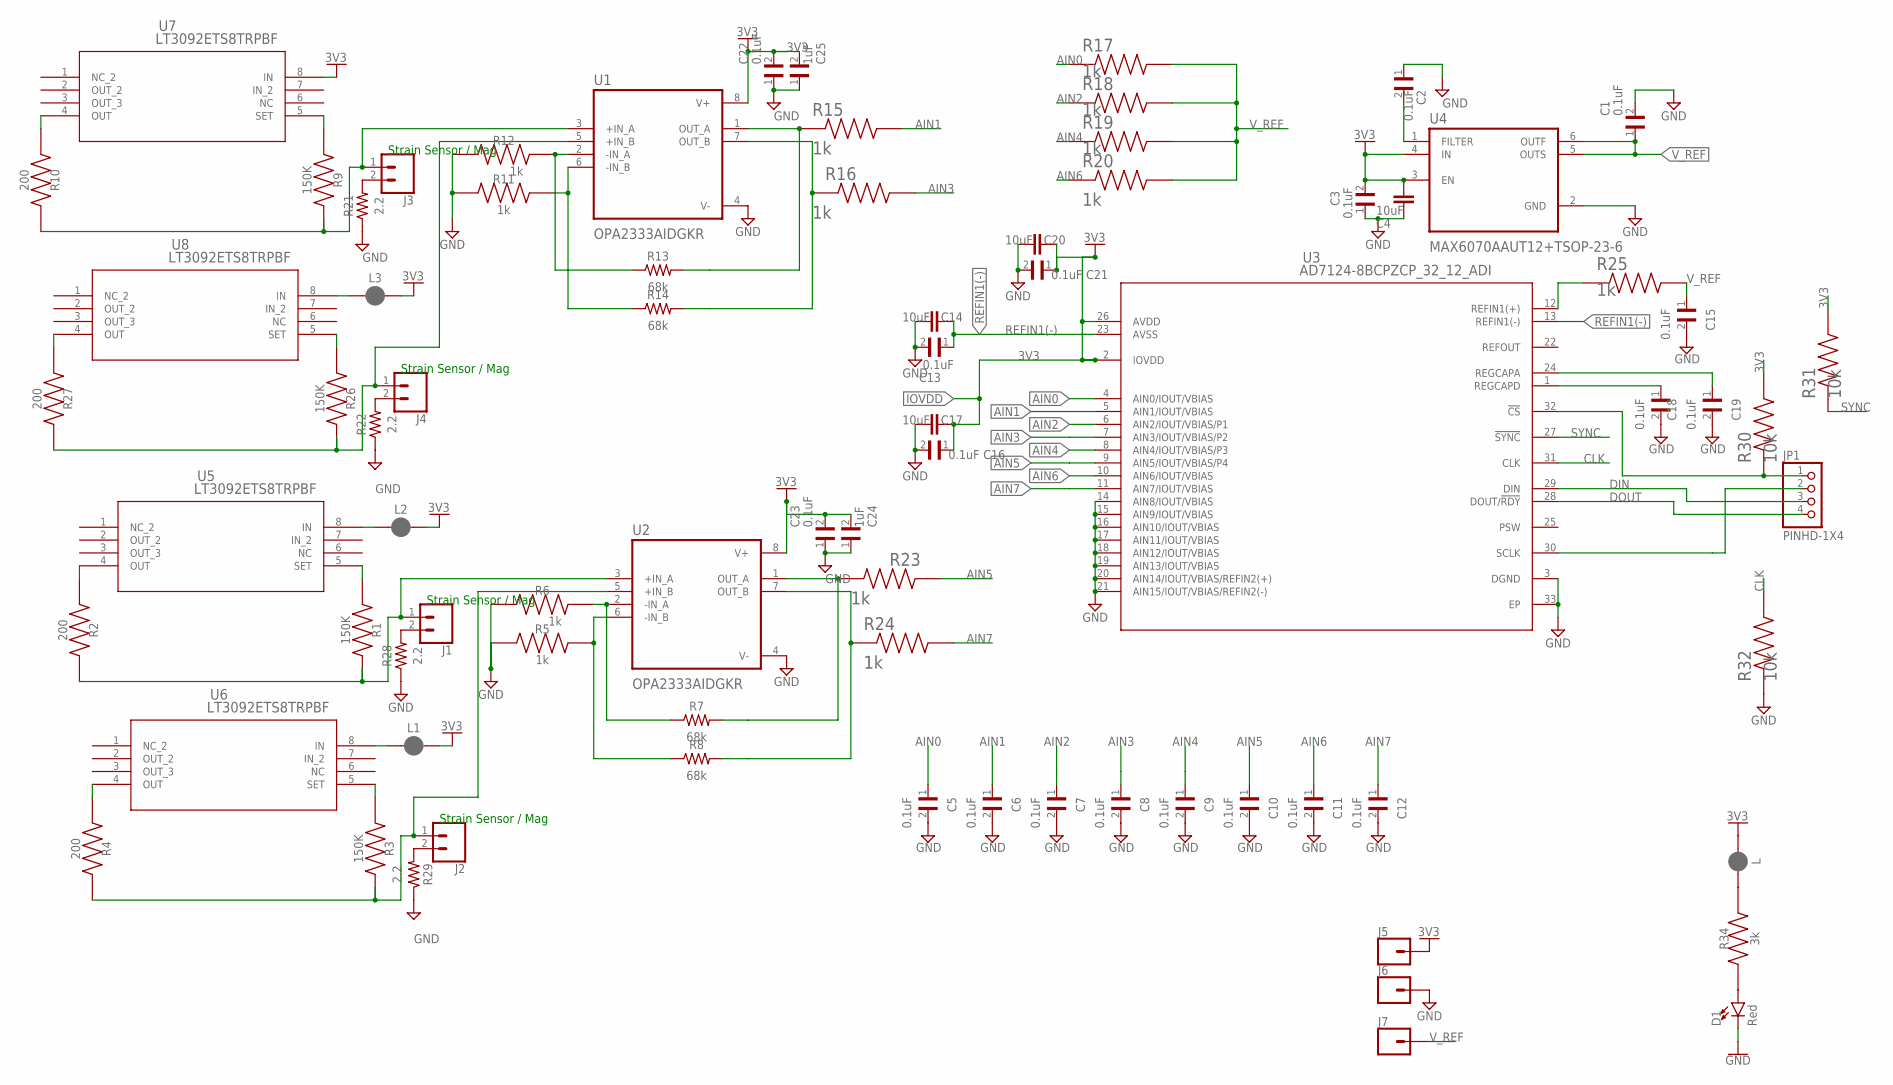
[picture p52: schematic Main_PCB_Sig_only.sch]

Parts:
C1, C2, C3, C5, C6, C7, C8, C9, C10, C11, C12, C13, C15, C16, C18, C19, C21, C22, C23: 0.1uF; CAPC0603X33N
C4, C14, C17, C20: 10uF; CAPC1005X60
C24, C25: 1uF; CAPC0603X33N
D1: Red; LED-0603
J1, J2, J3, J4: CONN_02; 1X02
J5, J6, J7: CONN_01PTH_LONGPAD; 1X01_LONGPAD
JP1: PINHD-1X4; 1X04
L, L1, L2, L3: JUMPER-SMT_2_NC_PASTE_NO-SILK; SMT-JUMPER_2_NC_PASTE_NO-SILK
R1, R3, R9, R26: 150K; RESC0603X26N
R2, R4, R10, R27: 200; RESC0603X26N
R5, R6, R11, R12, R15, R16, R17, R18, R19, R20, R23, R24, R25: 1k; RESC0603X26N
R7, R8, R13, R14: 68k; RESC1608X60
R21, R22, R28, R29: 2.2; RESC1608X60
R30, R31, R32: 10k; RESC0603X26N
R34: 3k; RESC0603X26N
U1, U2: OPA2333AIDGKR; SOP65P490X110-8N
U3: AD7124-8BCPZCP_32_12_ADI; CP_32_12_ADI
U4: MAX6070AAUT12+TSOP-23-6; SOT95P280X145-6N
U5, U6, U7, U8: LT3092ETS8TRPBF; TSOT-23_TS8

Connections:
3V3: C3.2, C4.2, C16.1, C17.1, C20.1, C21.1, C22.2, C23.2, C24.2, C25.2, J5.1, L.1, L1.2, L2.2, L3.2, R30.2, R31.2, U1.8 (V+), U2.8 (V+), U3.2 (IOVDD), U3.26 (AVDD), U4.3 (EN), U4.4 (IN), U7.8 (IN)
+IN_A1: J3.1, R9.2, R10.2, U1.3 (+IN_A)
+IN_A2: J1.1, R1.2, R2.2, U2.3 (+IN_A)
+IN_B1: J4.1, R26.2, R27.2, U1.5 (+IN_B)
+IN_B2: J2.1, R3.2, R4.2, U2.5 (+IN_B)
-IN_A1: R12.2, R13.1, U1.2 (-IN_A)
-IN_A2: R6.2, R7.1, U2.2 (-IN_A)
-IN_B1: R11.2, R14.1, U1.6 (-IN_B)
-IN_B2: R5.2, R8.1, U2.6 (-IN_B)
AIN0: C5.1, R17.1, U3.4 (AIN0/IOUT/VBIAS)
AIN1: C6.1, R15.2, U3.5 (AIN1/IOUT/VBIAS)
AIN2: C7.1, R18.1, U3.6 (AIN2/IOUT/VBIAS/P1)
AIN3: C8.1, R16.2, U3.7 (AIN3/IOUT/VBIAS/P2)
AIN4: C9.1, R19.1, U3.8 (AIN4/IOUT/VBIAS/P3)
AIN5: C10.1, R23.2, U3.9 (AIN5/IOUT/VBIAS/P4)
AIN6: C11.1, R20.1, U3.10 (AIN6/IOUT/VBIAS)
AIN7: C12.1, R24.2, U3.11 (AIN7/IOUT/VBIAS)
CLK: R32.2, U3.31 (CLK)
CS: JP1.1, R30.1, U3.32 (!CS)
DIN: JP1.3, U3.29 (DIN)
DOUT: JP1.4, U3.28 (DOUT/!RDY)
GND: C1.2, C2.1, C3.1, C4.1, C5.2, C6.2, C7.2, C8.2, C9.2, C10.2, C11.2, C12.2, C13.2, C14.2, C15.2, C16.2, C17.2, C18.2, C19.2, C20.2, C21.2, C22.1, C23.1, C24.1, C25.1, D1.C, J6.1, R5.1, R6.1, R11.1, R12.1, R21.1, R22.1, R28.1, R29.1, R32.1, U1.4 (V-), U2.4 (V-), U3.3 (DGND), U3.14 (AIN8/IOUT/VBIAS), U3.15 (AIN9/IOUT/VBIAS), U3.16 (AIN10/IOUT/VBIAS), U3.17 (AIN11/IOUT/VBIAS), U3.18 (AIN12/IOUT/VBIAS), U3.19 (AIN13/IOUT/VBIAS), U3.20 (AIN14/IOUT/VBIAS/REFIN2(+)), U3.21 (AIN15/IOUT/VBIAS/REFIN2(-)), U3.33 (EP), U4.2 (GND)
I_OUT1: R10.1, U7.4 (OUT)
I_OUT2: R27.1, U8.4 (OUT)
I_OUT3: R2.1, U5.4 (OUT)
I_OUT4: R4.1, U6.4 (OUT)
I_SET1: R9.1, U7.5 (SET)
I_SET2: R26.1, U8.5 (SET)
I_SET3: R1.1, U5.5 (SET)
I_SET4: R3.1, U6.5 (SET)
unnamed: L1.1, U6.8 (IN)
unnamed: C2.2, U4.1 (FILTER)
unnamed: J3.2, R21.2
unnamed: J4.2, R22.2
unnamed: J1.2, R28.2
unnamed: J2.2, R29.2
unnamed: L.2, R34.2
unnamed: D1.A, R34.1
unnamed: L2.1, U5.8 (IN)
unnamed: L3.1, U8.8 (IN)
OUT_A1: R13.2, R15.1, U1.1 (OUT_A)
OUT_A2: R7.2, R23.1, U2.1 (OUT_A)
OUT_B1: R14.2, R16.1, U1.7 (OUT_B)
OUT_B2: R8.2, R24.1, U2.7 (OUT_B)
REFIN1(+): R25.1, U3.12 (REFIN1(+))
REFIN1(-): C13.1, C14.1, U3.13 (REFIN1(-)), U3.23 (AVSS)
REGCAPA: C19.1, U3.24 (REGCAPA)
REGCAPD: C18.1, U3.1 (REGCAPD)
SCLK: JP1.2, U3.30 (SCLK)
SYNC: R31.1, U3.27 (!SYNC)
V_REF: C1.1, C15.1, J7.1, R17.2, R18.2, R19.2, R20.2, R25.2, U4.5 (OUTS), U4.6 (OUTF)

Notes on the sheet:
Strain Sensor / Mag

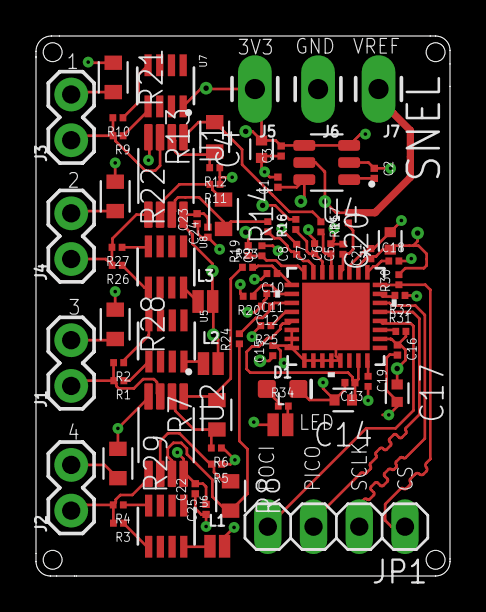
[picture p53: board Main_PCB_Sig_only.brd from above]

Board: 4 copper layers, 23.0 x 30.0 mm, 79 parts (0 on the bottom side), 51 nets.

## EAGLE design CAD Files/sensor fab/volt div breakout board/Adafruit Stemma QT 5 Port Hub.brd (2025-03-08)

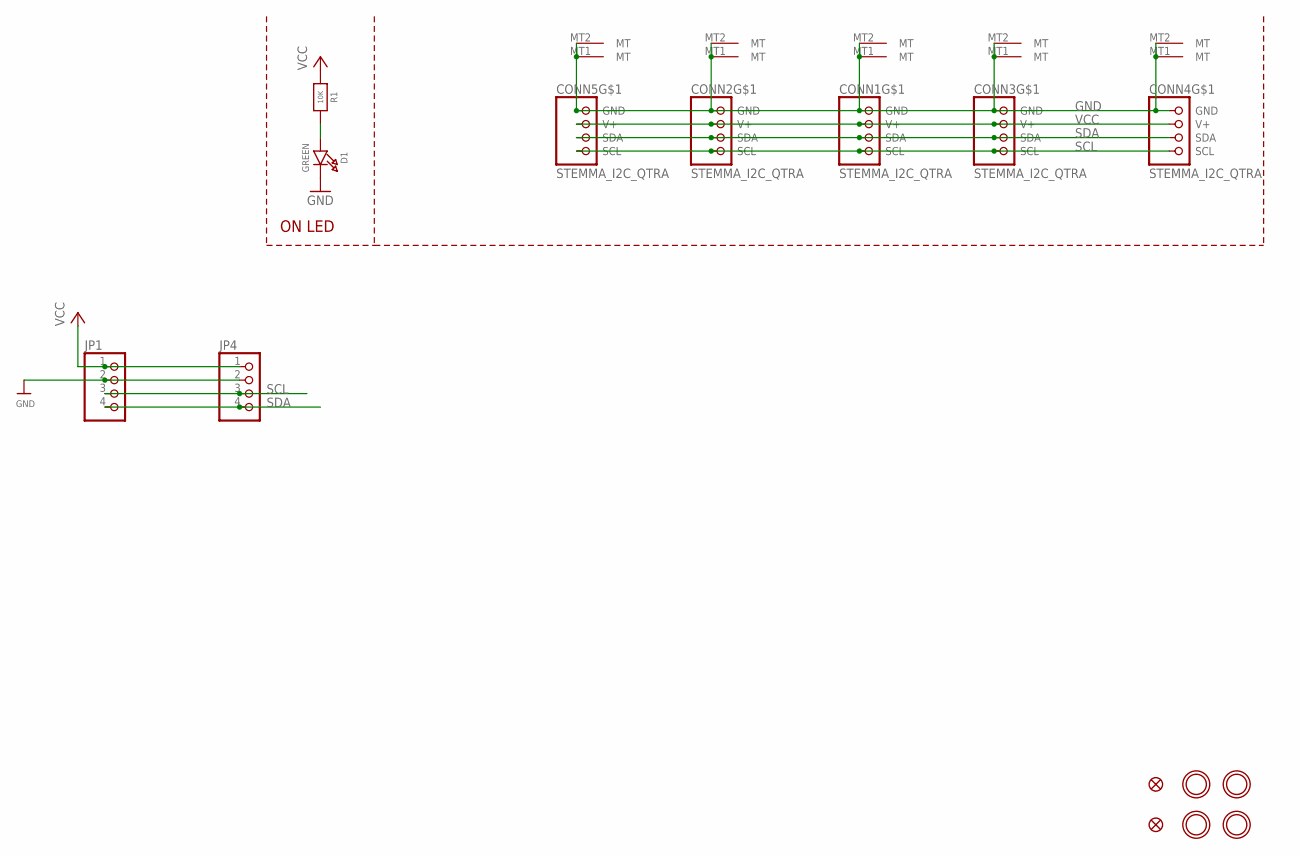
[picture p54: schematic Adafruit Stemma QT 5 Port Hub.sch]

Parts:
CONN1, CONN2, CONN3, CONN4, CONN5: STEMMA_I2C_QTRA; JST_SH4_RA
D1: GREEN; CHIPLED_0603_NOOUTLINE
FID3, FID4: FIDUCIAL_1MM
JP1, JP4: HEADER-1X476MIL; 1X04_ROUND_76
R1: 10K; 0603-NO
U$1, U$17, U$19, U$21: MOUNTINGHOLE2.5; MOUNTINGHOLE_2.5_PLATED

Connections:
GND: CONN1.1 (GND), CONN1.MT1 (MT), CONN1.MT2 (MT), CONN2.1 (GND), CONN2.MT1 (MT), CONN2.MT2 (MT), CONN3.1 (GND), CONN3.MT1 (MT), CONN3.MT2 (MT), CONN4.1 (GND), CONN4.MT1 (MT), CONN4.MT2 (MT), CONN5.1 (GND), CONN5.MT1 (MT), CONN5.MT2 (MT), D1.C, JP1.2, JP4.2
unnamed: D1.A, R1.2
SCL: CONN1.4 (SCL), CONN2.4 (SCL), CONN3.4 (SCL), CONN4.4 (SCL), CONN5.4 (SCL), JP1.3, JP4.3
SDA: CONN1.3 (SDA), CONN2.3 (SDA), CONN3.3 (SDA), CONN4.3 (SDA), CONN5.3 (SDA), JP1.4, JP4.4
VCC: CONN1.2 (V+), CONN2.2 (V+), CONN3.2 (V+), CONN4.2 (V+), CONN5.2 (V+), JP1.1, JP4.1, R1.1

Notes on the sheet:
ON LED

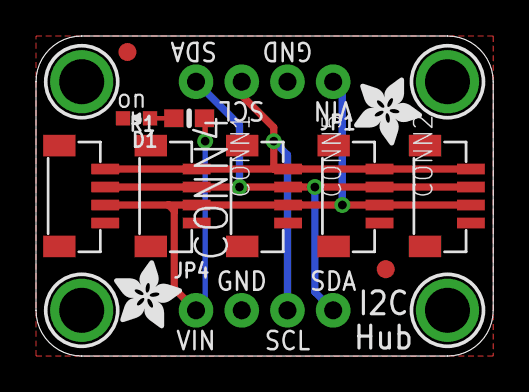
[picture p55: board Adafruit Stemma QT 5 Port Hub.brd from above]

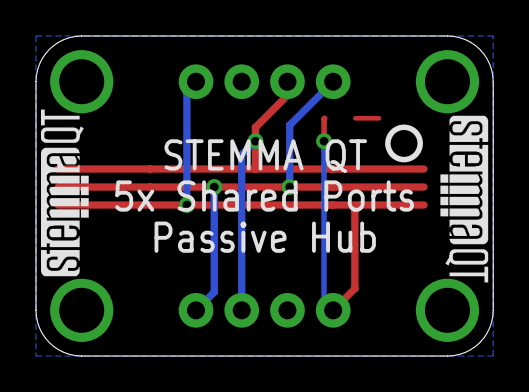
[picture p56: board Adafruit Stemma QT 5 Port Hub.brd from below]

Board: 2 copper layers, 25.4 x 17.8 mm, 20 parts (3 on the bottom side), 5 nets.

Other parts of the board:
U$2, U$3: ADAFRUIT_3.5MM
U$25: PCBFEAT-REV-040
U$30, U$31: STEMMAQT

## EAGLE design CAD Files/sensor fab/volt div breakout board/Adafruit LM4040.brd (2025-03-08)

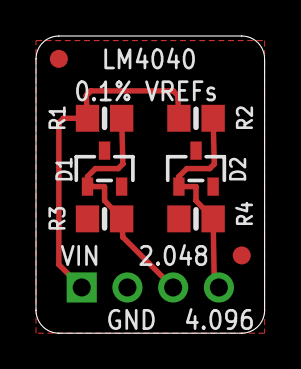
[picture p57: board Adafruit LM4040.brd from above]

Board: 2 copper layers, 12.7 x 16.5 mm, 10 parts (1 on the bottom side), 4 nets.

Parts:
D1: LM4040AIM3-2.0/NOPB; SOT23-R
D2: LM4040AIM3-4.1/NOPB; SOT23-R
FID1, FID2: FIDUCIAL""; FIDUCIAL_1MM
JP1: 1X04_ROUND
R1, R2: 750; 0805-NO
R3, R4: 10K; 0805-NO
U$5: ADAFRUIT_5MM

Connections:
2.048V: D1.1, JP1.3, R1.1, R3.1
4.096V: D2.1, JP1.4, R2.1, R4.1
GND: D1.2, D2.2, JP1.2, R3.2, R4.2
VIN: JP1.1, R1.2, R2.2

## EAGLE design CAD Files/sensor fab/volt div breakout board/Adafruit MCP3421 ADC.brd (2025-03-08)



Board: 2 copper layers, 25.4 x 17.8 mm, 37 parts (9 on the bottom side), 8 nets.

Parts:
C3: 10uF; 0805-NO
C4: 0.1uF; 0603-NO
CONN3, CONN4: STEMMA_I2C_QT; JST_SH4
D1: GREEN; CHIPLED_0603_NOOUTLINE
FB1: FERRITE; 0603-NO
FID3, FID4: FIDUCIAL_1MM
JP1: 1X06_ROUND_70
PLABEL0: PLABEL0
PLABEL1: PLABEL1
PLABEL2: PLABEL2
PLABEL3: PLABEL3
PLABEL4: PLABEL4
PLABEL5: PLABEL5
PLABEL6: PLABEL6
PLABEL7: PLABEL7
PLABEL8: PLABEL8
PLABEL9: PLABEL9
PLABEL10: PLABEL10
PLABEL11: PLABEL11
PLABEL12: PLABEL12
R1: 10K Pack; RESPACK_4X0603
U$2, U$7: SYMBOL_PLUS
U$4, U$5: SYMBOL_MINUS
U$8: PCBFEAT-REV-040
U$9: MCP3421; SOT23-6
U$20, U$21, U$25, U$27: MOUNTINGHOLE2.5; MOUNTINGHOLE_2.5_PLATED
U$29: ADAFRUIT_3.5MM
U$31, U$32: STEMMAQT
X1: 3.5mm Terminal Block; TERMBLOCK_1X2-3.5MM

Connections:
GND: C3.2, C4.2, CONN3.1, CONN3.MT1, CONN3.MT2, CONN4.1, CONN4.MT1, CONN4.MT2, D1.C, JP1.2, R1.1, R1.8, U$9.2
unnamed: D1.A, R1.5
SCL: CONN3.4, CONN4.4, JP1.3, R1.3, U$9.3
SDA: CONN3.3, CONN4.3, JP1.4, R1.2, U$9.4
VCC: C3.1, CONN3.2, CONN4.2, FB1.2, JP1.1, R1.4, R1.6, R1.7
VDD: C4.1, FB1.1, U$9.5
VIN+: JP1.5, U$9.1, X1.1
VIN-: JP1.6, U$9.6, X1.2

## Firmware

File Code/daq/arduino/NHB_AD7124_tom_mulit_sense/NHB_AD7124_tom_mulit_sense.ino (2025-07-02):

#include <NHB_AD7124.h>

#define CH_COUNT 4  // 4 differential pairs (AIN0–1, AIN2–3, AIN4–5, AIN6–7)

// Buffer for ADC readings
double buf[CH_COUNT];
const uint8_t csPin = 5;
double exRefV = 2.048;
AD7124_BurnoutCurrents burnout;
Ad7124 adc(csPin, 4000000);  // SPI @ 4 MHz

#define CONVMODE AD7124_OpMode_Continuous  // Continuous conversion mode
int filterSelBits = 100;  // Adjust this based on noise/speed tradeoff

void setup() {
  Serial.begin(115200);
  while (!Serial) {
    ;  // Wait for Serial to be ready
  }

  Serial.println("AD7124 - 4 Differential Channel Read Example");

  // Initialize ADC
  adc.begin();

  // Set mode and power
  adc.setAdcControl(CONVMODE, AD7124_FullPower, true);  // true = enable reference

  // Configure Setup 4:
  // - External reference (e.g., 3.3V)
  // - Gain = 32 → ±103 mV input range
  // - Bipolar mode (true)
  adc.setup[0].setConfig(AD7124_Ref_ExtRef1, AD7124_Gain_32, true, burnout, exRefV);
  adc.setup[0].setFilter(AD7124_Filter_SINC3, filterSelBits);
  adc.setup[1].setConfig(AD7124_Ref_ExtRef1, AD7124_Gain_32, true, burnout, exRefV);
  adc.setup[1].setFilter(AD7124_Filter_SINC3, filterSelBits);
  adc.setup[2].setConfig(AD7124_Ref_ExtRef1, AD7124_Gain_32, true, burnout, exRefV);
  adc.setup[2].setFilter(AD7124_Filter_SINC3, filterSelBits);
  adc.setup[3].setConfig(AD7124_Ref_ExtRef1, AD7124_Gain_32, true, burnout, exRefV);
  adc.setup[3].setFilter(AD7124_Filter_SINC3, filterSelBits);

  // Enable 4 fully differential input channels using Setup 4
  adc.setChannel(0, 0, AD7124_Input_AIN4, AD7124_Input_AVSS, true);  // CH0
  adc.setChannel(1, 1, AD7124_Input_AIN1, AD7124_Input_AVSS, true);  // CH1
  adc.setChannel(2, 2, AD7124_Input_AIN2, AD7124_Input_AVSS, true);  // CH2
  adc.setChannel(3, 3, AD7124_Input_AIN3, AD7124_Input_AVSS, true);  // CH3
}

void loop() {
  const int activeChannels[CH_COUNT] = {0, 1, 2, 3};  // Channel indices in ADC

  for (int i = 0; i < CH_COUNT; i++) {
    buf[i] = adc.readVolts(activeChannels[i]);  // Read differential voltage
    Serial.print(buf[i], 6);
    Serial.print("\t");
  }

  Serial.println();
  delay(6);  // Adjust for sampling rate / readability
}

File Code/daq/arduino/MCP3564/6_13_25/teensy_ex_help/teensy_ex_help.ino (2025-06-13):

// Arduino Uno-Compatible MCP3564 Control Code with SPI Communication Check
#include <Arduino.h>
#include <SPI.h>

const float Current_Command_Array[] = {0};
#define Time_Scale 5
#define IGBT_PWM_PIN 6        // Use PWM-capable pin
#define ADC_INT_PIN 2         // Must support external interrupt
#define SPI_CS_PIN 10

#define Shunt_R 0.0005
#define Ramp_Rate 2000
#define Current_Limit 200
#define Battery_Voltage_Limit 2.90
#define IGBT_Temp_Limit 100
#define Battery_Temp_Limit 60

#define P 0.5
#define I 0.1

enum OSR : uint8_t {
  OSR_128 = 0x02,
};
enum Channel : uint8_t {
  SE_0 = 0x00,
  SE_1 = 0x01,
  SE_2 = 0x02,
  SE_3 = 0x03,
};

constexpr double Current_Sense_Gain = 1 / (Shunt_R * 20);
constexpr double Ramp_Rate_Per_Millisecond = (double)Ramp_Rate / 1000;

// SPI Constants
constexpr uint32_t SPI_Speed = 2000000;
constexpr uint8_t ADDR = 0b01000000;
constexpr uint8_t FAST_CMD = 0b00000000;
constexpr uint8_t CONV = 0b00101000;
constexpr uint8_t STBY = 0b00101100;
constexpr uint8_t RESET = 0b00111000;
constexpr uint8_t INC_WRITE = 0b00000010;
constexpr uint8_t CONFIG0_ADDR = 0x04;
constexpr uint8_t CONFIG1_ADDR = 0x08;
constexpr uint8_t CONFIG2_ADDR = 0x0C;
constexpr uint8_t CONFIG3_ADDR = 0x10;
constexpr uint8_t IRQ_ADDR = 0x14;
constexpr uint8_t MUX_ADDR = 0x18;
constexpr uint8_t ADC_REG = 0x00;
constexpr uint8_t READ = 0x01;
constexpr uint8_t DEVICE_ID_ADDR = 0x0D;

// Config Register Values
constexpr uint8_t CONFIG0 = 0b11010010;
constexpr uint8_t CONFIG1 = (OSR_128 << 2);
constexpr uint8_t CONFIG2 = 0b10001011;
constexpr uint8_t CONFIG3 = 0b11110000;
constexpr uint8_t IRQ = 0b01110110;
constexpr uint8_t MUX = 0x00; // SE_0 selected

// Globals
volatile double Current_Command = 0;
volatile double Integral = 0;
volatile double Battery_Current = 0;
volatile double Battery_Voltage = 0;
volatile double IGBT_Temp = 0;
volatile double Battery_Temp = 0;
volatile uint32_t Time = 0;
volatile double Current_Array[4] = {0};
volatile uint32_t Current_Array_Index = 0;
volatile double Voltage_Array[2] = {0};
volatile uint32_t Voltage_Array_Index = 0;
bool Running = false;
uint32_t Last_Time = 0;
uint32_t i = 0;
double Current_Command_Temp = 0;
uint32_t Time_Delta_OLD = 0;

// Helper: SPI transfer 32-bit
uint32_t SPI_transfer32(uint32_t data) {
  uint32_t value = 0;
  value |= (uint32_t)SPI.transfer((data >> 24) & 0xFF) << 24;
  value |= (uint32_t)SPI.transfer((data >> 16) & 0xFF) << 16;
  value |= (uint32_t)SPI.transfer((data >> 8) & 0xFF) << 8;
  value |= (uint32_t)SPI.transfer(data & 0xFF);
  return value;
}

// SPI Communication Check
void checkMCP3564Connection() {
  SPI.beginTransaction(SPISettings(SPI_Speed, MSBFIRST, SPI_MODE0));
  digitalWrite(SPI_CS_PIN, LOW);
  SPI.transfer(ADDR | DEVICE_ID_ADDR | READ);
  uint8_t id1 = SPI.transfer(0x00);
  uint8_t id2 = SPI.transfer(0x00);
  uint8_t id3 = SPI.transfer(0x00);
  digitalWrite(SPI_CS_PIN, HIGH);
  SPI.endTransaction();

  Serial.println("Raw SDO response from MCP3564:");
  Serial.print("0x"); Serial.print(id1, HEX); Serial.print(" 0x"); Serial.print(id2, HEX); Serial.print(" 0x"); Serial.println(id3, HEX);
}

void ADC_Init() {
  SPI.begin();
  pinMode(SPI_CS_PIN, OUTPUT);
  digitalWrite(SPI_CS_PIN, HIGH);
  delay(100);

  checkMCP3564Connection();

  SPI.beginTransaction(SPISettings(SPI_Speed, MSBFIRST, SPI_MODE0));
  digitalWrite(SPI_CS_PIN, LOW);
  SPI.transfer(ADDR | RESET | FAST_CMD);
  digitalWrite(SPI_CS_PIN, HIGH);
  SPI.endTransaction();
  delay(5);

  SPI.beginTransaction(SPISettings(SPI_Speed, MSBFIRST, SPI_MODE0));
  digitalWrite(SPI_CS_PIN, LOW);
  SPI.transfer(ADDR | CONFIG0_ADDR | INC_WRITE);
  SPI.transfer(CONFIG0);
  SPI.transfer(CONFIG1);
  SPI.transfer(CONFIG2);
  SPI.transfer(CONFIG3);
  SPI.transfer(IRQ);
  SPI.transfer(MUX);
  digitalWrite(SPI_CS_PIN, HIGH);
  SPI.endTransaction();
}

void setup() {
  Serial.begin(115200);
  pinMode(IGBT_PWM_PIN, OUTPUT);
  analogWrite(IGBT_PWM_PIN, 0);
  pinMode(ADC_INT_PIN, INPUT);
  attachInterrupt(digitalPinToInterrupt(ADC_INT_PIN), [] {}, FALLING); // dummy ISR
  ADC_Init();
  Last_Time = micros();
}

void loop() {
  // Placeholder loop
}

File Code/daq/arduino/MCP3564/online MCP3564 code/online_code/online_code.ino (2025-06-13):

#include <SPI.h>

#define SPI_CS_PIN 10  // Chip select for MCP3564

#define VREF 3.3      // External voltage reference (e.g., 3.3 V)
#define OSR_SETTING 0x0F  // OSR_98304 = ~1 sample/sec

// MCP3564 SPI command constants
#define ADDR           0b01000000
#define RESET          0b00111000
#define CONVERT        0b00101000
#define CONFIG0_ADDR   0x04
#define CONFIG1_ADDR   0x08
#define CONFIG2_ADDR   0x0C
#define CONFIG3_ADDR   0x10
#define MUX_ADDR       0x18
#define ADC_READ       0x00
#define READ_FLAG      0x01

// MCP3564 register values
#define CONFIG0  (0b11010010 | (1 << 5))  // Internal clock enabled
#define CONFIG1  (OSR_SETTING << 2)       // OSR_128
#define CONFIG2  0b10001110  // External VREF, PGA = 64
#define CONFIG3  0b11110000  // Continuous conversion mode
#define MUX      0b00000000  // SE_0 (AIN0 w.r.t. AGND)

// === Setup ===
void setup() {
  Serial.begin(115200);
  pinMode(SPI_CS_PIN, OUTPUT);
  digitalWrite(SPI_CS_PIN, HIGH);
  SPI.begin();

  delay(100);  // Allow MCP3564 to boot
  resetADC();
  configureADC();
  startConversion();

  Serial.println("MCP3564 initialized with PGA=128, external VREF = 3.3V");
}

// === Main Loop ===
void loop() {
  int32_t adc_code = readADC();

  // Convert ADC code to voltage (measured voltage = code * VREF / PGA / 2^23)
  float voltage = (adc_code / 8388607.0) * (VREF / 128.0);

  Serial.print("ADC Code: ");
  Serial.print(adc_code);
  Serial.print(" | Voltage: ");
  Serial.println(voltage, 6);  // Print with 6 decimal places

  delay(500);  // ~10 Hz read rate
}

// === Helper Functions ===
void resetADC() {
  digitalWrite(SPI_CS_PIN, LOW);
  SPI.beginTransaction(SPISettings(2000000, MSBFIRST, SPI_MODE0));
  SPI.transfer(ADDR | RESET);  // Fast command: RESET
  digitalWrite(SPI_CS_PIN, HIGH);
  SPI.endTransaction();
  delay(5);
}

void configureADC() {
  digitalWrite(SPI_CS_PIN, LOW);
  SPI.beginTransaction(SPISettings(2000000, MSBFIRST, SPI_MODE0));
  SPI.transfer(ADDR | CONFIG0_ADDR);  // Start writing at CONFIG0
  SPI.transfer(CONFIG0);
  SPI.transfer(CONFIG1);
  SPI.transfer(CONFIG2);  // Use external VREF, PGA = 128
  SPI.transfer(CONFIG3);
  SPI.transfer(MUX);
  digitalWrite(SPI_CS_PIN, HIGH);
  SPI.endTransaction();
  delay(10);
}

void startConversion() {
  digitalWrite(SPI_CS_PIN, LOW);
  SPI.beginTransaction(SPISettings(2000000, MSBFIRST, SPI_MODE0));
  SPI.transfer(ADDR | CONVERT);  // Begin continuous conversion
  digitalWrite(SPI_CS_PIN, HIGH);
  SPI.endTransaction();
}

int32_t readADC() {
  uint32_t raw = 0;
  digitalWrite(SPI_CS_PIN, LOW);
  SPI.beginTransaction(SPISettings(2000000, MSBFIRST, SPI_MODE0));
  SPI.transfer(ADDR | ADC_READ | READ_FLAG);  // Read ADC register
  for (int i = 0; i < 4; i++) {
    raw <<= 8;
    raw |= SPI.transfer(0x00);
  }
  digitalWrite(SPI_CS_PIN, HIGH);
  SPI.endTransaction();

  // Extract signed 24-bit data (bits 0–25), discard tag
  int32_t value = ((int32_t)(raw & 0x01FFFFFF) << 7) >> 7;
  return value;
}

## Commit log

2024-10-29 Added CAD and Blender Files
    Added CAD and Blender Files
    [1501 mg servo.0002.ipt, 1501 mg servo.ipt, Adafruit_BNO055_AP214.0001.ipt, Adafruit_BNO055_AP214.STEP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]
2024-11-04 CAD Files Added
    CAD Files Added
    [0p03_total_thickness.0005.ipt, 0p03_total_thickness.ipt, Assembly1.0001.iam, Assembly1.iam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]
2024-11-14 Phil Code Add
    Phil Code Add
    [Bending_data_1_loop_11_13_24_v1.csv, Bending_data_1_loop_11_13_24_v2.csv, Phil_Test.csv, bender PCB.fzz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]
2024-11-14 Added single loop strain abs sensor
    Added single loop strain abs sensor
    [basic strain gauge 0p01.0001.ipt, basic strain gauge 0p01.ipt, basic strain gauge 0p02 real.stl, basic strain gauge 0p02.ipt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]
2024-12-12 New Files
    New Files
    [Bending_data_abs_1p53_11_27_24_0deg_reapply_2.csv, Bending_data_abs_1p53_11_27_24_0deg_reapply_3.csv, Bending_data_abs_1p53_11_27_24_0deg_reapply_4.csv, Bendin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]
2024-12-18 new servo code
    [dynamic_test.csv]
2024-12-18 Code and Data Added
    [Bending_data_abs_1p53_11_27_24_0deg_reapply_1.csv, Bending_data_abs_1p53_11_27_24_0deg_reapply_2.csv, Bending_data_abs_1p53_11_27_24_0deg_reapply_3.csv, Bendin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]
2024-12-19 new code and data
    [Bending_data_abs_1p93_0deg_12_18_24.csv]
2025-01-07 Consolidated Files and Folders
    Consolidated Files and Folders
    [Bending_data_abs_1p987_dyn_v2_1sec_0p08th_12_18_24.csv, dynamic_test.csv]
2025-01-09 added code
    [Bending_data_20250109_092904_818.csv, Bending_data_abs_1p987_dyn_v2_1sec_0p08th_12_18_24.csv, abs thick measure.xlsx, dynamic_test.csv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]
2025-01-13 Organized CAD folders and added images
    [1p5 sensor for show.ipt, Assembly of hinge.0001.iam, Assembly of hinge.iam, Assembly1.iam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]
2025-01-14 Added Folders
    [bender PCB for presentation.fzz, bender PCB.fzz]
2025-01-16 adding xls sheet download to keep paired with the repo
    [data_25_01_14.xlsx]
2025-01-21 added to analysis
    [Bending_data_abs_1p53_11_27_24_0deg_reapply_1.csv, Bending_data_abs_1p53_11_27_24_0deg_reapply_2.csv, Bending_data_abs_1p53_11_27_24_0deg_reapply_3.csv, Bendin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]
2025-01-22 changed master csv file
    [data_25_01_14.xlsx]
2025-01-23 updated analysis files
    [data_25_01_14.xlsx]
2025-02-04 new reapplication data
    [Bending_data_abs_1p7_abs_1p7_1st_reapply_2_4_25.csv, Bending_data_abs_1p7_abs_1p7_2nd_reapply_2_4_25.csv, Bending_data_abs_1p7_abs_1p7_3rd_reapply_2_4_25.csv, 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]
2025-02-06 new reapplication data and analysis
    [Bending_data_abs_1p758_2nd_reapply_2_6_25.csv, Bending_data_abs_1p758_3rd_reapply_2_6_25.csv, Bending_data_abs_1p758_4th_reapply_2_6_25.csv, Bending_data_abs_1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]
2025-02-11 Sensor Fab and Mis Data
    Collected new misalignment data on two additional samples. Also created cad files and png image for sensor fabrication image for future paper
    [Assembly1.0001.iam, Assembly1.iam, Bending_data_abs_1p685_0deg_2_11_25.csv, Bending_data_abs_1p732_0deg_2_11_25.csv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]
2025-02-13 added bender_class methods
    [data_25_01_14.xlsx]
2025-02-18 updated bender_class and added analysis code
    updated bender_class , added analysis code, and created prelim fig 1
    [data_25_01_14.xlsx]
2025-02-27 updated error analysis
    [data_25_01_14.xlsx]
2025-03-05 added CAD files, analysis, and fig 1
    [acetone bottle.SLDPRT, acetone dissolve.SLDASM, acetone.SLDPRT, base plate.SLDPRT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]
2025-03-08 updates fab image renderings
    [100 ohm resistor.SLDPRT, 2 screw terminal.SLDPRT, 5 pin header.SLDPRT, Adafruit LM4040.brd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]
2025-03-13 added fig 1 images
    [3.7v li-ion 500mah Battery.step, Bending_data_20250109_092904_818.csv, Bending_data_20250313_135051_078.csv, Seeed Studio XIAO RP2040 v26.step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]
2025-03-14 added new tab for PK data check of fig 1
    [data_25_01_14.xlsx]
2025-03-17 data updates to PK tab
    [data_25_01_14.xlsx]
2025-03-18 changed some csv file names and made sure Preeya code worked on my end
    corrected some csv file names to consistent with rest of filenames.
    [130817_6-Hand with sensors.SLDASM, Bending_data_abs_1p53_11_27_24_0deg_reapply_2.csv, Bending_data_abs_1p53_11_27_24_0deg_reapply_3.csv, Bending_data_abs_1p758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]
2025-03-18 conducted ~ 10 retests wtih 16 ADC and 8x amp
    [Bending_data_abs_1p732_0deg_retest_3_18_25.csv, Bending_data_abs_1p732_0deg_retest_v2_3_18_25.csv, Bending_data_abs_1p732_0deg_retest_v3_3_18_25.csv, Bending_d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]
2025-03-20 New voltage divider circuit and retests
    [Bending_data_abs_1p758_retest_v5_3_20_25.csv, Bending_data_abs_1p758_retest_v6_3_20_25.csv, Bending_data_abs_1p758_retest_v7_3_20_25.csv, Bending_data_abs_1p75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]
2025-04-09 added data, daq code, and modified analysis
    added data, daq code, and modified analysis delta norm to take into account negative and pos adc values
    [Bending_data_abs_1p987_retest_v4_3_25_25.csv, Bending_data_abs_1p987_retest_v5_3_27_25.csv, Bending_data_abs_1p987_retest_v6_3_31_25.csv, Bending_data_abs_1pxx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]
2025-04-09 updated 4_9_25 presentation
    [voltage divider 3_28_25.fzz]
2025-04-11 Python DAQ, new CSV files, and Analsys.py change
    Added a GUI to the python daq so that user can enter sample info. Also, csv auto saved in correct folder. Changed analysis accuracy method so that instead in incremeting angle of min accuracy by 1, i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
    [1.787_static_vs2_v1_4_11_25.csv, 1.86_static_v1_4_10_25.csv, 1.86_static_v2_4_10_25.csv, 1.86_static_v3_4_10_25.csv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]
2025-04-15 Acquired More Data, Changed analysis.py to include quadratic fitting
    [1.85_static_v1_4_15_25.csv, 1.85_static_v2_4_15_25.csv, 1.875_static_v1_4_15_25.csv, 1.98_static_v1_4_15_25.csv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]
2025-04-18 1 sample of reapplicaton and misalignment with Velcro...updated presentation
    [2.185_static_v1_4_17_25.csv, 2.185_static_v2_4_17_25.csv, 2.24_misalignment_v10_4_17_25.csv, 2.24_misalignment_v20_4_17_25.csv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]
2025-04-18 collected reapplication and misalignment data with velcro
    [2.27_reapplication_v1_4_18_25.csv, 2.27_reapplication_v2_4_18_25.csv, 2.27_reapplication_v3_4_18_25.csv, 2.27_reapplication_v4_4_18_25.csv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]
2025-04-22 finished testing misalignment, reapplication, and length data. All code updated
    [1.86_misalignment_v10_2nd_attempt_4_22_25.csv, 1.86_misalignment_v10_4_22_25.csv, 1.86_misalignment_v20_4_22_25.csv, 1.86_reapplication_v1_4_22_25.csv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]
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2025-04-29 improved organization of datafile,
    [Bending_data_10_14_2024_v1.csv, Bending_data_10_14_2024_v11.csv, Bending_data_10_14_2024_v2.csv, Bending_data_10_14_2024_v3.csv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]
2025-04-30 Updated data spreadsheet and reapplication analysis code
    [data_25_01_14.xlsx]
2025-04-30 updated datasheet for clarity one last time
    [data_25_01_14.xlsx]
2025-05-05 new data acquired and new arduino daq
    [1.86_static_v1_331x_test_5_5_25.csv, 1.86_static_vADS1115_test_5_5_25.csv, data_25_01_14.xlsx]
2025-05-12 new data
    [1.53_static_v1_velcro_5_7_25.csv, 1.53_static_v2_velcro_5_7_25.csv, 1.5_static_v1_velcro_5_12_25.csv, 1.5_static_v2_velcro_5_12_25.csv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]
2025-05-14 circuit design for camera setup and new reapp analysis
    [Camera Parts BOM.xlsx]
2025-05-23 new data acquired for model testing
    [0.8ohm_static_v1_5_22_25.csv, 0.8ohm_static_v2_5_22_25.csv, 0.8ohm_static_v3_5_22_25.csv, 0.8ohm_static_v4_5_22_25.csv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]
2025-06-06 new data and data vs model analysis
    [2.1_static_v1_silpoxy_0.03_5_28_25.csv, 2.1_static_v1_silpoxy_0.03_6_2_25.csv, 2.1_static_v1_silpoxy_0.03_6_4_25.csv, 2.1_static_v1_silpoxy_0.03_nobend_5_28_25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]
2025-06-06 updated model analysis notebook
    [data_25_01_14.xlsx]
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2025-07-18 new camera, DAQ, and adc code!
    [Strain Gauge Watch BOM.xlsx, test.csv]
2025-08-13 added camera analysis code
    [2025_08_07_09_21_23_DLC_3D.csv, assembly with alignment.0002.iam, assembly with alignment.iam, basic strain gauge 0p02 w align.0003.ipt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]
2025-08-13 new dlc class methods
    [8.13_DLC_3D.csv, data_adc_2025_08_13_10_55_21.csv, data_imu_2025_08_13_10_55_21.csv, data_rotenc_2025_08_13_10_55_21.csv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]
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2025-08-18 updated figures and analysis code
    [data_adc_2025_08_15_18_01_27.csv, data_adc_2025_08_15_18_02_22.csv, data_adc_2025_08_15_18_02_54.csv, data_adc_2025_08_15_18_03_24.csv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]
2025-08-22 updated analysis.py and camera jupyter notebook
    [2025_08_20_18_37_05_DLC_3D.csv, camera-1-2025_08_20_18_37_05DLC_Resnet50_0815Aug16shuffle1_snapshot_010.csv, camera-2-2025_08_20_18_37_05DLC_Resnet50_0815Aug16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]
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2025-09-05 strain vs encoder code
    added notebook code for calibration of strain sensor on autobender using rpi breakout board
    [data_adc_2025_09_04_16_28_17.csv, data_imu_2025_09_04_16_28_17.csv, data_rotenc_2025_09_04_16_28_17.csv, data_spacebar_2025_09_04_16_28_17.csv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]
2025-09-10 updated analysis
    [data_adc_2025_09_04_20_37_12.csv, data_adc_2025_09_04_20_42_03.csv, data_adc_2025_09_04_20_43_43.csv, data_adc_2025_09_04_20_44_12.csv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]
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2025-11-14 adc error analysis complete
    [camera-1-2025_11_02_14_29_07_B_medmDLC_Resnet50_SOR4_11_02Nov3shuffle1_snapshot_010.csv, camera-1-2025_11_02_14_29_26_B_medmDLC_Resnet50_SOR4_11_02Nov3shuffle1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]
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

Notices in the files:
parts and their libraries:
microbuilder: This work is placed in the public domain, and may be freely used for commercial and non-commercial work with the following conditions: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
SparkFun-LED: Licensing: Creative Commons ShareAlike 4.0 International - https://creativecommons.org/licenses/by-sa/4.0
